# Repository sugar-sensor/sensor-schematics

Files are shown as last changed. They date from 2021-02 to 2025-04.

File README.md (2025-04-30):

# Description
Electrical and mechanical schematics for sugar sensor. 
Includes PCB design and BOM + Gerber files for sensor production
Repository has 2 branches: v1 and v2. Both are based on MAX86141 AFE to work with LEDs. The difference between v1 and v2 are the following:
- v1 uses 3 LEDS (RED, GREEN, BLUE) as light source (non-coherent) while v2 uses 7mW 650nm RED laser (coherent)
- v1 uses AD5933 BioZ controller while v2 uses MAX30002 BioZ controller
- in v2 the main board dependency is removed. Main board replaced with external [TinyPICO](https://www.tinypico.com/) board and add-ons. Sensor board is stackable

## Project notes
1. The main reason to move from v1 to v2 of the sensor board is failed tests on non-coherent light sources. "Failed" means prediction based on these measurements didn't work.
2. Version 2 deprecates "main" folder with all the schematics for main board (controller). Sensor board is stacked with TiniPICO development board and it is stacked with RGB IPS Display shield from add-ons menu.
3. Sensor board programming, testing and obtaining the results is done using [MAX32630FHTR](https://www.analog.com/en/resources/evaluation-hardware-and-software/evaluation-boards-kits/max32630fthr.html) application platform. Development was done in [Mbed Studio](https://os.mbed.com/studio/)

## Structure
- **hull** for the wearable device
- **lib** is custom libraries for KiCad
- **main** is a mainboad schematics. Valid only for v1. Not tested and not produced. 
- **mech** is 3D models for the KiCad component representation on PCB
- **sensor** is sensor schematic, board, BOM, gerbers for production. Both versions were tested and produced

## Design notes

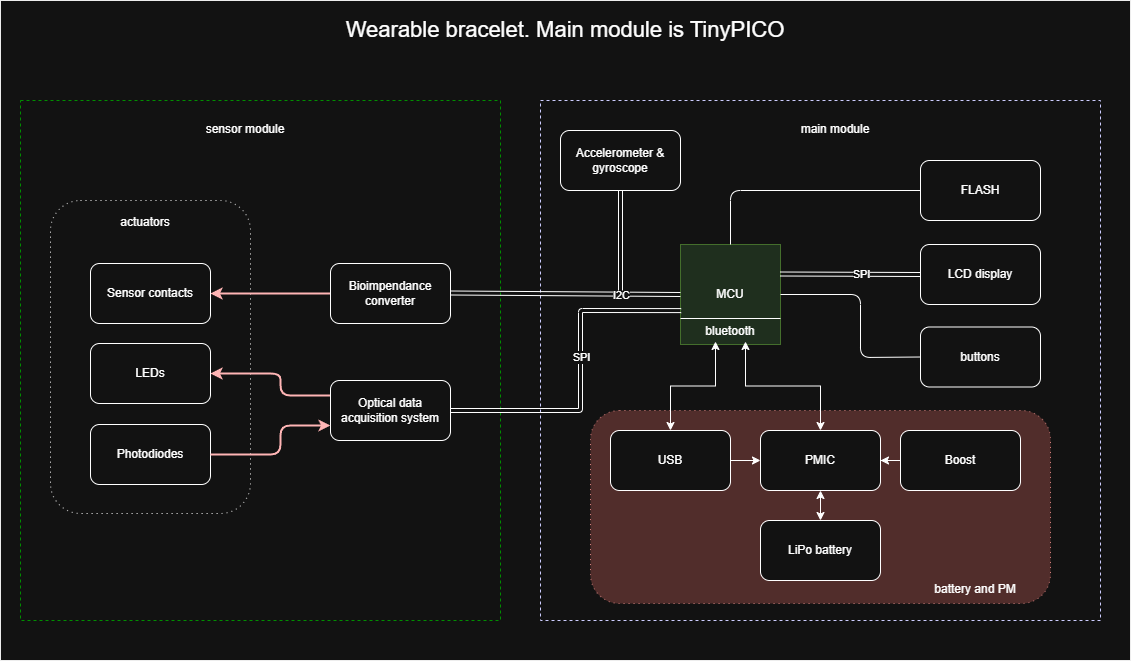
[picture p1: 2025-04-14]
block_diagram.png

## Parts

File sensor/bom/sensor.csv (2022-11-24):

Source: | C:\Users\Vadim\Projects\Horace\sensor\sensor.kicad_sch
Date: | 24.11.2022 15:50:27
Tool: | Eeschema (6.0.8)
Generator: | C:\Program Files\KiCad\6.0\bin\scripting\plugins/bom_csv_grouped_by_value.py
Component Count: | 44
Individual Components:
Item | Qty | Reference(s) | Value | LibPart | Footprint | Datasheet | Arrow Part Number | Arrow Price/Stock | Description | Digikey Part Number | Height | Manufacturer | Manufacturer Part Number | Manufacturer_Name | Manufacturer_Part_Number | Mouser Part Number | Mouser Price/Stock | Mouser part number | Mouser parts/stock | Price
 |  | C1 | 10pF | Device:C_Small | Capacitor_SMD:C_0402_1005Metric | https://www.mouser.ee/datasheet/2/447/UPY-GPHC_X5R_4V-to-50V_25-1131599.pdf |  |  |  | 311-3777-2-ND |  | Yageo | CC0402KRNPO7BN100 |  |  |  | https://www.mouser.ee/ProductDetail/Yageo/CC0402MRX5R5BB106/?qs=zEY9bCHj09eCmUJdZuS5Lg%3D%3D |  |  | 0.1
 |  | C2 | 10pF | Device:C_Small | Capacitor_SMD:C_0402_1005Metric | https://www.mouser.ee/datasheet/2/447/UPY-GPHC_X5R_4V-to-50V_25-1131599.pdf |  |  |  | 311-3777-2-ND |  | Yageo | CC0402KRNPO7BN100 |  |  |  | https://www.mouser.ee/ProductDetail/Yageo/CC0402MRX5R5BB106/?qs=zEY9bCHj09eCmUJdZuS5Lg%3D%3D |  |  | 0.1
 |  | C3 | 47pF | Device:C_Small | Capacitor_SMD:C_0402_1005Metric | https://www.mouser.ee/datasheet/2/447/UPY-GPHC_X5R_4V-to-50V_25-1131599.pdf |  |  |  | 311-3751-2-ND |  | Yageo | CC0402JRNPO8BN470 |  |  |  | https://www.mouser.ee/ProductDetail/Yageo/CC0402MRX5R5BB106/?qs=zEY9bCHj09eCmUJdZuS5Lg%3D%3D |  |  | 0.22
 |  | C4 | 1uF | Device:C_Small | Capacitor_SMD:C_0402_1005Metric | http://www.easyflip.co.uk/Farnell_element14_2013_UK/book.html?page=1145 |  |  |  | 311-1438-2-ND |  | Yageo | CC0402KRX5R5BB105 |  |  |  | https://www.mouser.ee/ProductDetail/Yageo/CC0402KRX5R5BB105/?qs=AgBp2OyFlx8OsRLdvCJiRw%3D%3D |  |  | 0.09
 |  | C5 | 10uF | Device:C_Small | Capacitor_SMD:C_0402_1005Metric | https://www.mouser.ee/datasheet/2/447/UPY-GPHC_X5R_4V-to-50V_25-1131599.pdf |  |  |  | 311-1729-2-ND |  | Yageo | CC0402MRX5R5BB106 |  |  |  | https://www.mouser.ee/ProductDetail/Yageo/CC0402MRX5R5BB106/?qs=zEY9bCHj09eCmUJdZuS5Lg%3D%3D |  |  | 0.22
 |  | C6 | 47nF | Device:C_Small | Capacitor_SMD:C_0402_1005Metric | https://www.mouser.ee/datasheet/2/447/UPY-GPHC_X5R_4V-to-50V_25-1131599.pdf |  |  |  | 311-1688-2-ND |  | Yageo | CC0402KRX5R6BB473 |  |  |  | https://www.mouser.ee/ProductDetail/Yageo/CC0402MRX5R5BB106/?qs=zEY9bCHj09eCmUJdZuS5Lg%3D%3D |  |  | 0.22
 |  | C7 | 47nF | Device:C_Small | Capacitor_SMD:C_0402_1005Metric | https://www.mouser.ee/datasheet/2/447/UPY-GPHC_X5R_4V-to-50V_25-1131599.pdf |  |  |  | 311-1688-2-ND |  | Yageo | CC0402KRX5R6BB473 |  |  |  | https://www.mouser.ee/ProductDetail/Yageo/CC0402MRX5R5BB106/?qs=zEY9bCHj09eCmUJdZuS5Lg%3D%3D |  |  | 0.22
 |  | C8 | 10uF | Device:C_Small | Capacitor_SMD:C_0402_1005Metric | https://www.mouser.ee/datasheet/2/447/UPY-GPHC_X5R_4V-to-50V_25-1131599.pdf |  |  |  | 311-1729-2-ND |  | Yageo | CC0402MRX5R5BB106 |  |  |  | https://www.mouser.ee/ProductDetail/Yageo/CC0402MRX5R5BB106/?qs=zEY9bCHj09eCmUJdZuS5Lg%3D%3D |  |  | 0.22
 |  | C9 | 0.1uF | Device:C_Small | Capacitor_SMD:C_0402_1005Metric | https://www.mouser.ee/datasheet/2/447/UPY-GPHC_X5R_4V-to-50V_25-1131599.pdf |  |  |  | 311-3340-2-ND |  | Yageo | CC0402KRX5R5BB104 |  |  |  | https://www.mouser.ee/ProductDetail/Yageo/CC0402KRX5R5BB104/?qs=T%2F3nPWKqOSbG4z8ii3LyCg%3D%3D |  |  | 0.09
 |  | C10 | 0.1uF | Device:C_Small | Capacitor_SMD:C_0402_1005Metric | https://www.mouser.ee/datasheet/2/447/UPY-GPHC_X5R_4V-to-50V_25-1131599.pdf |  |  |  | 311-3340-2-ND |  | Yageo | CC0402KRX5R5BB104 |  |  |  | https://www.mouser.ee/ProductDetail/Yageo/CC0402KRX5R5BB104/?qs=T%2F3nPWKqOSbG4z8ii3LyCg%3D%3D |  |  | 0.09
 |  | C11 | 1nF | Device:C_Small | Capacitor_SMD:C_0402_1005Metric | https://www.mouser.ee/datasheet/2/447/UPY-GPHC_X5R_4V-to-50V_25-1131599.pdf |  |  |  | 13-CC0402JRNPO7BN102TR-ND |  | Yageo | CC0402JRNPO7BN102 |  |  |  | https://www.mouser.ee/ProductDetail/Yageo/CC0402MRX5R5BB106/?qs=zEY9bCHj09eCmUJdZuS5Lg%3D%3D |  |  | 0.22
 |  | C12 | 10uF | Device:C_Small | Capacitor_SMD:C_0402_1005Metric | https://www.mouser.ee/datasheet/2/447/UPY-GPHC_X5R_4V-to-50V_25-1131599.pdf |  |  |  | 311-1729-2-ND |  | Yageo | CC0402MRX5R5BB106 |  |  |  | https://www.mouser.ee/ProductDetail/Yageo/CC0402MRX5R5BB106/?qs=zEY9bCHj09eCmUJdZuS5Lg%3D%3D |  |  | 0.22
 |  | C13 | 10uF | Device:C_Small | Capacitor_SMD:C_0402_1005Metric | https://www.mouser.ee/datasheet/2/447/UPY-GPHC_X5R_4V-to-50V_25-1131599.pdf |  |  |  | 311-1729-2-ND |  | Yageo | CC0402MRX5R5BB106 |  |  |  | https://www.mouser.ee/ProductDetail/Yageo/CC0402MRX5R5BB106/?qs=zEY9bCHj09eCmUJdZuS5Lg%3D%3D |  |  | 0.22
 |  | C14 | 1uF | Device:C_Small | Capacitor_SMD:C_0402_1005Metric | http://www.easyflip.co.uk/Farnell_element14_2013_UK/book.html?page=1145 |  |  |  | 311-1438-2-ND |  | Yageo | CC0402KRX5R5BB105 |  |  |  | https://www.mouser.ee/ProductDetail/Yageo/CC0402KRX5R5BB105/?qs=AgBp2OyFlx8OsRLdvCJiRw%3D%3D |  |  | 0.09
 |  | C15 | 1uF | Device:C_Small | Capacitor_SMD:C_0402_1005Metric | http://www.easyflip.co.uk/Farnell_element14_2013_UK/book.html?page=1145 |  |  |  | 311-1438-2-ND |  | Yageo | CC0402KRX5R5BB105 |  |  |  | https://www.mouser.ee/ProductDetail/Yageo/CC0402KRX5R5BB105/?qs=AgBp2OyFlx8OsRLdvCJiRw%3D%3D |  |  | 0.09
 |  | C16 | 10uF | Device:C_Small | Capacitor_SMD:C_0402_1005Metric | https://www.mouser.ee/datasheet/2/447/UPY-GPHC_X5R_4V-to-50V_25-1131599.pdf |  |  |  | 311-1729-2-ND |  | Yageo | CC0402MRX5R5BB106 |  |  |  | https://www.mouser.ee/ProductDetail/Yageo/CC0402MRX5R5BB106/?qs=zEY9bCHj09eCmUJdZuS5Lg%3D%3D |  |  | 0.22
 |  | C17 | 1uF | Device:C_Small | Capacitor_SMD:C_0402_1005Metric | http://www.easyflip.co.uk/Farnell_element14_2013_UK/book.html?page=1145 |  |  |  | 311-1438-2-ND |  | Yageo | CC0402KRX5R5BB105 |  |  |  | https://www.mouser.ee/ProductDetail/Yageo/CC0402KRX5R5BB105/?qs=AgBp2OyFlx8OsRLdvCJiRw%3D%3D |  |  | 0.09
 |  | C18 | 1uF | Device:C_Small | Capacitor_SMD:C_0402_1005Metric | http://www.easyflip.co.uk/Farnell_element14_2013_UK/book.html?page=1145 |  |  |  | 311-1438-2-ND |  | Yageo | CC0402KRX5R5BB105 |  |  |  | https://www.mouser.ee/ProductDetail/Yageo/CC0402KRX5R5BB105/?qs=AgBp2OyFlx8OsRLdvCJiRw%3D%3D |  |  | 0.09
 |  | C19 | 0.1uF | Device:C_Small | Capacitor_SMD:C_0402_1005Metric | https://www.mouser.ee/datasheet/2/447/UPY-GPHC_X5R_4V-to-50V_25-1131599.pdf |  |  |  | 311-3340-2-ND |  | Yageo | CC0402KRX5R5BB104 |  |  |  | https://www.mouser.ee/ProductDetail/Yageo/CC0402KRX5R5BB104/?qs=T%2F3nPWKqOSbG4z8ii3LyCg%3D%3D |  |  | 0.09
 |  | C20 | 10uF | Device:C_Small | Capacitor_SMD:C_0402_1005Metric | https://www.mouser.ee/datasheet/2/447/UPY-GPHC_X5R_4V-to-50V_25-1131599.pdf |  |  |  | 311-1729-2-ND |  | Yageo | CC0402MRX5R5BB106 |  |  |  | https://www.mouser.ee/ProductDetail/Yageo/CC0402MRX5R5BB106/?qs=zEY9bCHj09eCmUJdZuS5Lg%3D%3D |  |  | 0.22
 |  | C21 | 1uF | Device:C_Small | Capacitor_SMD:C_0402_1005Metric | http://www.easyflip.co.uk/Farnell_element14_2013_UK/book.html?page=1145 |  |  |  | 311-1438-2-ND |  | Yageo | CC0402KRX5R5BB105 |  |  |  | https://www.mouser.ee/ProductDetail/Yageo/CC0402KRX5R5BB105/?qs=AgBp2OyFlx8OsRLdvCJiRw%3D%3D |  |  | 0.09
 |  | D1 | RLD65NZX1-00A | Horace:RLD65NZX1-00A | Horace:RLD85PZJ400A | https://fscdn.rohm.com/en/products/databook/datasheet/opto/laser_diode/red/rld65pzx300a012-e.pdf |  |  | 635nm Red Single Mode Laser Diode |  | 4.6 |  |  | ROHM Semiconductor | RLD65NZX1-00A | 755-RLD65NZX1-00A | https://www.mouser.co.uk/ProductDetail/ROHM-Semiconductor/RLD65NZX1-00A?qs=vmHwEFxEFR8OdK%252BWr0L3QQ%3D%3D
 |  | D2 | VEMD8081 | Horace:VEMD8081 | Horace:VEMD8081 | https://www.vishay.com/docs/80218/vemd8081.pdf |  |  | High speed and high sensitive PIN photodiode with enhanced sensitivity for visible light, 4.8 x 2.5 x 0.48 package, Radiant sensitive area (in mm2): 5.4 |  | 0.53 |  |  | Vishay | VEMD8081 | 78-VEMD8081 | https://www.mouser.co.uk/ProductDetail/Vishay-Semiconductors/VEMD8081?qs=hd1VzrDQEGhZjg8mME3%2FzQ%3D%3D
 |  | D3 | VEMD8081 | Horace:VEMD8081 | Horace:VEMD8081 | https://www.vishay.com/docs/80218/vemd8081.pdf |  |  | High speed and high sensitive PIN photodiode with enhanced sensitivity for visible light, 4.8 x 2.5 x 0.48 package, Radiant sensitive area (in mm2): 5.4 |  | 0.53 |  |  | Vishay | VEMD8081 | 78-VEMD8081 | https://www.mouser.co.uk/ProductDetail/Vishay-Semiconductors/VEMD8081?qs=hd1VzrDQEGhZjg8mME3%2FzQ%3D%3D
 |  | IC1 | MAX30002CWV+ | Horace:MAX30002CWV+ | Horace:MAX30002CWV | https://componentsearchengine.com/Datasheets/1/MAX30002CWV+.pdf |  |  | Analog Front End - AFE Bio Potential AFE | MAX30002CWV+-ND | 0.69 |  |  | Maxim Integrated | MAX30002CWV+ | 700-MAX30002CWV+ | https://www.mouser.co.uk/ProductDetail/Maxim-Integrated/MAX30002CWV%2b?qs=gTYE2QTfZfRSACHOszRGvQ%3D%3D
 |  | IC2 | LP5900TLX-2.7_NOPB | Horace:LP5900TLX-2.7_NOPB | Horace:BGA4C50P2X2_105X108X68 | http://www.ti.com/lit/gpn/LP5900 |  |  | 150mA Ultralow-Noise LDO for RF and Analog Circuits Requires No Bypass Capacitor |  | 0.675 |  |  | Texas Instruments | LP5900TLX-2.7/NOPB | 926-LP5900TLX27NOPB | https://www.mouser.co.uk/ProductDetail/Texas-Instruments/LP5900TLX-27-NOPB?qs=8uBHJDVwVqwI%252Br0sr7pGhg%3D%3D
 |  | IC3 | MAX86141ENP+T | sensor-rescue:MAX86141ENP+-Horace | Horace:BGA20C40P5X4_205X185X50 | https://www.mouser.ee/datasheet/2/256/MAX86140-1139682.pdf |  |  | MAXIM INTEGRATED PRODUCTS - MAX86141ENP+ - PULSE OXIMETER/HEART RATE SENSOR, WLP-20 | MAX86141ENP+TCT-ND | 0.5 | Maxim Integrated | MAX86141ENP+T | Maxim Integrated | MAX86141ENP+ | 700-MAX86141ENP+T | https://www.mouser.ee/ProductDetail/Maxim-Integrated/MAX86141ENP%2bT?qs=1mbolxNpo8eXAkUx4%252BsdhQ%3D%3D |  |  | 6.25
 |  | IC4 | SIT1532AC | Horace:SIT1532AC-J5-DCC-32.768D | Horace:SIT1532ACJ5DCC32768D | https://www.sitime.com/datasheet/SiT1532 | SIT1532AC-J5-DCC-32.768D | https://www.arrow.com/en/products/sit1532acj5dcc32.768d/sitime?region=nac | Oscillator MEMS 0.032768MHz +/-75ppm (Stability) LVCMOS 52% 1.8V/2.5V/3.3V 4-Pin CSP SMD T/R |  | 0.6 |  |  | SiTime | SIT1532AC-J5-DCC-32.768D | 788-1532ACJ5DCC32.7D | https://www.mouser.co.uk/ProductDetail/SiTime/SIT1532AC-J5-DCC-32768D?qs=dMZC7um9hO%2FgFQ4wFMXsCg%3D%3D
 |  | IC5 | LP5900TLX-1.8_NOPB | Horace:LP5900TLX-2.7_NOPB | Horace:BGA4C50P2X2_105X108X68 | http://www.ti.com/lit/gpn/LP5900 |  |  | 150mA Ultralow-Noise LDO for RF and Analog Circuits Requires No Bypass Capacitor |  | 0.675 |  |  | Texas Instruments | LP5900TLX-2.7/NOPB | 926-LP5900TLX27NOPB | https://www.mouser.co.uk/ProductDetail/Texas-Instruments/LP5900TLX-27-NOPB?qs=8uBHJDVwVqwI%252Br0sr7pGhg%3D%3D
 |  | J1 | Conn_01x10_Female | Connector:Conn_01x10_Female | Connector_PinSocket_2.54mm:PinSocket_1x10_P2.54mm_Vertical | https://www.mouser.ee/datasheet/2/276/3/0901471110_PCB_RECEPTACLES-2871466.pdf |  |  |  |  |  | Molex | 90147-1110 |  |  |  |  | 538-90147-1110 | https://www.mouser.ee/ProductDetail/Molex/90147-1110
 |  | J2 | Conn_01x10_Female | Connector:Conn_01x10_Female | Connector_PinSocket_2.54mm:PinSocket_1x10_P2.54mm_Vertical | https://www.mouser.ee/datasheet/2/276/3/0901471110_PCB_RECEPTACLES-2871466.pdf |  |  |  |  |  | Molex | 90147-1110 |  |  |  |  | 538-90147-1110 | https://www.mouser.ee/ProductDetail/Molex/90147-1110
 |  | J3 | Probe_01_male | sensor-rescue:Probe_01_male-Horace | Horace:Probe_01_male | https://www.mouser.ee/datasheet/2/273/223.7-1519985.pdf |  |  |  | ED10387-ND |  |  | 3977-1-00-15-00-00-03-0 |  |  |  | https://www.digikey.ee/products/en?keywords=3975-0-00-15-00-00-03-0 |  |  | 0.3
 |  | J4 | Probe_01_male | sensor-rescue:Probe_01_male-Horace | Horace:Probe_01_male | https://www.mouser.ee/datasheet/2/273/223.7-1519985.pdf |  |  |  | ED10387-ND |  |  | 3977-1-00-15-00-00-03-0 |  |  |  | https://www.digikey.ee/products/en?keywords=3975-0-00-15-00-00-03-0 |  |  | 0.3
 |  | J5 | Probe_01_male | sensor-rescue:Probe_01_male-Horace | Horace:Probe_01_male | https://www.mouser.ee/datasheet/2/273/223.7-1519985.pdf |  |  |  | ED10387-ND |  |  | 3977-1-00-15-00-00-03-0 |  |  |  | https://www.digikey.ee/products/en?keywords=3975-0-00-15-00-00-03-0 |  |  | 0.3
 |  | J6 | Probe_01_male | sensor-rescue:Probe_01_male-Horace | Horace:Probe_01_male | https://www.mouser.ee/datasheet/2/273/223.7-1519985.pdf |  |  |  | ED10387-ND |  |  | 3977-1-00-15-00-00-03-0 |  |  |  | https://www.digikey.ee/products/en?keywords=3975-0-00-15-00-00-03-0 |  |  | 0.3
 |  | R1 | 200 | Device:R_Small | Resistor_SMD:R_0402_1005Metric | https://www.mouser.ee/datasheet/2/427/crcwce3-1762584.pdf |  |  |  | 541-3995-2-ND |  | Vishay / Dale | CRCW0402200RFKEDC |  |  |  | https://www.mouser.ee/ProductDetail/Vishay-Dale/CRCW0402200RFKEDC?qs=E3Y5ESvWgWP6CT2hjJxX9A%3D%3D |  |  | 0.09
 |  | R2 | 200 | Device:R_Small | Resistor_SMD:R_0402_1005Metric | https://www.mouser.ee/datasheet/2/427/crcwce3-1762584.pdf |  |  |  | 541-3995-2-ND |  | Vishay / Dale | CRCW0402200RFKEDC |  |  |  | https://www.mouser.ee/ProductDetail/Vishay-Dale/CRCW0402200RFKEDC?qs=E3Y5ESvWgWP6CT2hjJxX9A%3D%3D |  |  | 0.09
 |  | R3 | 324k | Device:R_Small | Resistor_SMD:R_0402_1005Metric | https://www.mouser.ee/datasheet/2/427/crcwce3-1762584.pdf |  |  |  | 541-4894-2-ND |  | Vishay / Dale | CRCW0402324KFKEDC |  |  |  | https://www.mouser.ee/ProductDetail/Vishay-Dale/CRCW0402324KFKEDC?qs=E3Y5ESvWgWPWxHcYNHkI3g%3D%3D |  |  | 0.2
 |  | R4 | 0 | Device:R_Small | Resistor_SMD:R_0402_1005Metric | https://www.mouser.ee/datasheet/2/427/crcwce3-1762584.pdf |  |  |  | 541-4062-2-ND |  | Vishay / Dale | CRCW04020000Z0EDC |  |  |  | https://www.mouser.ee/ProductDetail/Vishay-Dale/CRCW04020000Z0EDC/ |  |  | 0.09
 |  | R5 | 1k | Device:R_Small | Resistor_SMD:R_0402_1005Metric | https://www.mouser.ee/datasheet/2/427/crcwce3-1762584.pdf |  |  |  | 541-3961-2-ND |  | Vishay / Dale | CRCW04021K00FKEDC |  |  |  | https://www.mouser.ee/ProductDetail/Vishay-Dale/CRCW04021K00FKEDC |  |  | 0.09
 |  | R6 | 1k | Device:R_Small | Resistor_SMD:R_0402_1005Metric | https://www.mouser.ee/datasheet/2/427/crcwce3-1762584.pdf |  |  |  | 541-3961-2-ND |  | Vishay / Dale | CRCW04021K00FKEDC |  |  |  | https://www.mouser.ee/ProductDetail/Vishay-Dale/CRCW04021K00FKEDC |  |  | 0.09
 |  | R7 | 1k | Device:R_Small | Resistor_SMD:R_0402_1005Metric | https://www.mouser.ee/datasheet/2/427/crcwce3-1762584.pdf |  |  |  | 541-3961-2-ND |  | Vishay / Dale | CRCW04021K00FKEDC |  |  |  | https://www.mouser.ee/ProductDetail/Vishay-Dale/CRCW04021K00FKEDC |  |  | 0.09
 |  | R8 | 0 | Device:R_Small | Resistor_SMD:R_0402_1005Metric | https://www.mouser.ee/datasheet/2/427/crcwce3-1762584.pdf |  |  |  | 541-4062-2-ND |  | Vishay / Dale | CRCW04020000Z0EDC |  |  |  | https://www.mouser.ee/ProductDetail/Vishay-Dale/CRCW04020000Z0EDC/ |  |  | 0.09
 |  | R9 | 0 | Device:R_Small | Resistor_SMD:R_0402_1005Metric | https://www.mouser.ee/datasheet/2/427/crcwce3-1762584.pdf |  |  |  | 541-4062-2-ND |  | Vishay / Dale | CRCW04020000Z0EDC |  |  |  | https://www.mouser.ee/ProductDetail/Vishay-Dale/CRCW04020000Z0EDC/ |  |  | 0.09
Collated Components:
Item | Qty | Reference(s) | Value | LibPart | Footprint | Datasheet | Arrow Part Number | Arrow Price/Stock | Description | Digikey Part Number | Height | Manufacturer | Manufacturer Part Number | Manufacturer_Name | Manufacturer_Part_Number | Mouser Part Number | Mouser Price/Stock | Mouser part number | Mouser parts/stock | Price
1 | 2 | C1, C2 | 10pF | Device:C_Small | Capacitor_SMD:C_0402_1005Metric | https://www.mouser.ee/datasheet/2/447/UPY-GPHC_X5R_4V-to-50V_25-1131599.pdf |  |  |  | 311-3777-2-ND |  | Yageo | CC0402KRNPO7BN100 |  |  |  | https://www.mouser.ee/ProductDetail/Yageo/CC0402MRX5R5BB106/?qs=zEY9bCHj09eCmUJdZuS5Lg%3D%3D |  |  | 0.1
2 | 1 | C3 | 47pF | Device:C_Small | Capacitor_SMD:C_0402_1005Metric | https://www.mouser.ee/datasheet/2/447/UPY-GPHC_X5R_4V-to-50V_25-1131599.pdf |  |  |  | 311-3751-2-ND |  | Yageo | CC0402JRNPO8BN470 |  |  |  | https://www.mouser.ee/ProductDetail/Yageo/CC0402MRX5R5BB106/?qs=zEY9bCHj09eCmUJdZuS5Lg%3D%3D |  |  | 0.22
3 | 6 | C4, C14, C15, C17, C18, C21 | 1uF | Device:C_Small | Capacitor_SMD:C_0402_1005Metric | http://www.easyflip.co.uk/Farnell_element14_2013_UK/book.html?page=1145 |  |  |  | 311-1438-2-ND |  | Yageo | CC0402KRX5R5BB105 |  |  |  | https://www.mouser.ee/ProductDetail/Yageo/CC0402KRX5R5BB105/?qs=AgBp2OyFlx8OsRLdvCJiRw%3D%3D |  |  | 0.09
4 | 6 | C5, C8, C12, C13, C16, C20 | 10uF | Device:C_Small | Capacitor_SMD:C_0402_1005Metric | https://www.mouser.ee/datasheet/2/447/UPY-GPHC_X5R_4V-to-50V_25-1131599.pdf |  |  |  | 311-1729-2-ND |  | Yageo | CC0402MRX5R5BB106 |  |  |  | https://www.mouser.ee/ProductDetail/Yageo/CC0402MRX5R5BB106/?qs=zEY9bCHj09eCmUJdZuS5Lg%3D%3D |  |  | 0.22
5 | 2 | C6, C7 | 47nF | Device:C_Small | Capacitor_SMD:C_0402_1005Metric | https://www.mouser.ee/datasheet/2/447/UPY-GPHC_X5R_4V-to-50V_25-1131599.pdf |  |  |  | 311-1688-2-ND |  | Yageo | CC0402KRX5R6BB473 |  |  |  | https://www.mouser.ee/ProductDetail/Yageo/CC0402MRX5R5BB106/?qs=zEY9bCHj09eCmUJdZuS5Lg%3D%3D |  |  | 0.22
6 | 3 | C9, C10, C19 | 0.1uF | Device:C_Small | Capacitor_SMD:C_0402_1005Metric | https://www.mouser.ee/datasheet/2/447/UPY-GPHC_X5R_4V-to-50V_25-1131599.pdf |  |  |  | 311-3340-2-ND |  | Yageo | CC0402KRX5R5BB104 |  |  |  | https://www.mouser.ee/ProductDetail/Yageo/CC0402KRX5R5BB104/?qs=T%2F3nPWKqOSbG4z8ii3LyCg%3D%3D |  |  | 0.09
7 | 1 | C11 | 1nF | Device:C_Small | Capacitor_SMD:C_0402_1005Metric | https://www.mouser.ee/datasheet/2/447/UPY-GPHC_X5R_4V-to-50V_25-1131599.pdf |  |  |  | 13-CC0402JRNPO7BN102TR-ND |  | Yageo | CC0402JRNPO7BN102 |  |  |  | https://www.mouser.ee/ProductDetail/Yageo/CC0402MRX5R5BB106/?qs=zEY9bCHj09eCmUJdZuS5Lg%3D%3D |  |  | 0.22
8 | 1 | D1 | RLD65NZX1-00A | Horace:RLD65NZX1-00A | Horace:RLD85PZJ400A | https://fscdn.rohm.com/en/products/databook/datasheet/opto/laser_diode/red/rld65pzx300a012-e.pdf |  |  | 635nm Red Single Mode Laser Diode |  | 4.6 |  |  | ROHM Semiconductor | RLD65NZX1-00A | 755-RLD65NZX1-00A | https://www.mouser.co.uk/ProductDetail/ROHM-Semiconductor/RLD65NZX1-00A?qs=vmHwEFxEFR8OdK%252BWr0L3QQ%3D%3D
9 | 2 | D2, D3 | VEMD8081 | Horace:VEMD8081 | Horace:VEMD8081 | https://www.vishay.com/docs/80218/vemd8081.pdf |  |  | High speed and high sensitive PIN photodiode with enhanced sensitivity for visible light, 4.8 x 2.5 x 0.48 package, Radiant sensitive area (in mm2): 5.4 |  | 0.53 |  |  | Vishay | VEMD8081 | 78-VEMD8081 | https://www.mouser.co.uk/ProductDetail/Vishay-Semiconductors/VEMD8081?qs=hd1VzrDQEGhZjg8mME3%2FzQ%3D%3D
10 | 1 | IC1 | MAX30002CWV+ | Horace:MAX30002CWV+ | Horace:MAX30002CWV | https://componentsearchengine.com/Datasheets/1/MAX30002CWV+.pdf |  |  | Analog Front End - AFE Bio Potential AFE | MAX30002CWV+-ND | 0.69 |  |  | Maxim Integrated | MAX30002CWV+ | 700-MAX30002CWV+ | https://www.mouser.co.uk/ProductDetail/Maxim-Integrated/MAX30002CWV%2b?qs=gTYE2QTfZfRSACHOszRGvQ%3D%3D
11 | 1 | IC2 | LP5900TLX-2.7_NOPB | Horace:LP5900TLX-2.7_NOPB | Horace:BGA4C50P2X2_105X108X68 | http://www.ti.com/lit/gpn/LP5900 |  |  | 150mA Ultralow-Noise LDO for RF and Analog Circuits Requires No Bypass Capacitor |  | 0.675 |  |  | Texas Instruments | LP5900TLX-2.7/NOPB | 926-LP5900TLX27NOPB | https://www.mouser.co.uk/ProductDetail/Texas-Instruments/LP5900TLX-27-NOPB?qs=8uBHJDVwVqwI%252Br0sr7pGhg%3D%3D
12 | 1 | IC3 | MAX86141ENP+T | sensor-rescue:MAX86141ENP+-Horace | Horace:BGA20C40P5X4_205X185X50 | https://www.mouser.ee/datasheet/2/256/MAX86140-1139682.pdf |  |  | MAXIM INTEGRATED PRODUCTS - MAX86141ENP+ - PULSE OXIMETER/HEART RATE SENSOR, WLP-20 | MAX86141ENP+TCT-ND | 0.5 | Maxim Integrated | MAX86141ENP+T | Maxim Integrated | MAX86141ENP+ | 700-MAX86141ENP+T | https://www.mouser.ee/ProductDetail/Maxim-Integrated/MAX86141ENP%2bT?qs=1mbolxNpo8eXAkUx4%252BsdhQ%3D%3D |  |  | 6.25
13 | 1 | IC4 | SIT1532AC | Horace:SIT1532AC-J5-DCC-32.768D | Horace:SIT1532ACJ5DCC32768D | https://www.sitime.com/datasheet/SiT1532 | SIT1532AC-J5-DCC-32.768D | https://www.arrow.com/en/products/sit1532acj5dcc32.768d/sitime?region=nac | Oscillator MEMS 0.032768MHz +/-75ppm (Stability) LVCMOS 52% 1.8V/2.5V/3.3V 4-Pin CSP SMD T/R |  | 0.6 |  |  | SiTime | SIT1532AC-J5-DCC-32.768D | 788-1532ACJ5DCC32.7D | https://www.mouser.co.uk/ProductDetail/SiTime/SIT1532AC-J5-DCC-32768D?qs=dMZC7um9hO%2FgFQ4wFMXsCg%3D%3D
14 | 1 | IC5 | LP5900TLX-1.8_NOPB | Horace:LP5900TLX-2.7_NOPB | Horace:BGA4C50P2X2_105X108X68 | http://www.ti.com/lit/gpn/LP5900 |  |  | 150mA Ultralow-Noise LDO for RF and Analog Circuits Requires No Bypass Capacitor |  | 0.675 |  |  | Texas Instruments | LP5900TLX-2.7/NOPB | 926-LP5900TLX27NOPB | https://www.mouser.co.uk/ProductDetail/Texas-Instruments/LP5900TLX-27-NOPB?qs=8uBHJDVwVqwI%252Br0sr7pGhg%3D%3D
15 | 2 | J1, J2 | Conn_01x10_Female | Connector:Conn_01x10_Female | Connector_PinSocket_2.54mm:PinSocket_1x10_P2.54mm_Vertical | https://www.mouser.ee/datasheet/2/276/3/0901471110_PCB_RECEPTACLES-2871466.pdf |  |  |  |  |  | Molex | 90147-1110 |  |  |  |  | 538-90147-1110 | https://www.mouser.ee/ProductDetail/Molex/90147-1110
16 | 4 | J3, J4, J5, J6 | Probe_01_male | sensor-rescue:Probe_01_male-Horace | Horace:Probe_01_male | https://www.mouser.ee/datasheet/2/273/223.7-1519985.pdf |  |  |  | ED10387-ND |  |  | 3977-1-00-15-00-00-03-0 |  |  |  | https://www.digikey.ee/products/en?keywords=3975-0-00-15-00-00-03-0 |  |  | 0.3
17 | 2 | R1, R2 | 200 | Device:R_Small | Resistor_SMD:R_0402_1005Metric | https://www.mouser.ee/datasheet/2/427/crcwce3-1762584.pdf |  |  |  | 541-3995-2-ND |  | Vishay / Dale | CRCW0402200RFKEDC |  |  |  | https://www.mouser.ee/ProductDetail/Vishay-Dale/CRCW0402200RFKEDC?qs=E3Y5ESvWgWP6CT2hjJxX9A%3D%3D |  |  | 0.09
18 | 1 | R3 | 324k | Device:R_Small | Resistor_SMD:R_0402_1005Metric | https://www.mouser.ee/datasheet/2/427/crcwce3-1762584.pdf |  |  |  | 541-4894-2-ND |  | Vishay / Dale | CRCW0402324KFKEDC |  |  |  | https://www.mouser.ee/ProductDetail/Vishay-Dale/CRCW0402324KFKEDC?qs=E3Y5ESvWgWPWxHcYNHkI3g%3D%3D |  |  | 0.2
19 | 3 | R4, R8, R9 | 0 | Device:R_Small | Resistor_SMD:R_0402_1005Metric | https://www.mouser.ee/datasheet/2/427/crcwce3-1762584.pdf |  |  |  | 541-4062-2-ND |  | Vishay / Dale | CRCW04020000Z0EDC |  |  |  | https://www.mouser.ee/ProductDetail/Vishay-Dale/CRCW04020000Z0EDC/ |  |  | 0.09
20 | 3 | R5, R6, R7 | 1k | Device:R_Small | Resistor_SMD:R_0402_1005Metric | https://www.mouser.ee/datasheet/2/427/crcwce3-1762584.pdf |  |  |  | 541-3961-2-ND |  | Vishay / Dale | CRCW04021K00FKEDC |  |  |  | https://www.mouser.ee/ProductDetail/Vishay-Dale/CRCW04021K00FKEDC |  |  | 0.09

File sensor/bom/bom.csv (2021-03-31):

Reference | Value | Footprint | Datasheet | Digikey Part Number | Manufacturer | Manufacturer Part Number | Mouser Price/Stock | Price | Description | Digikey_ref | Height | Manufacturer Name | Mouser Part Number | Arrow Part Number | Arrow Price/Stock
C4 | 22uF | Capacitor_SMD:C_0402_1005Metric | https://www.mouser.ee/datasheet/2/447/UPY-GPHC_X5R_4V-to-50V_25-1131599.pdf | 311-3479-2-ND | Yageo | CC0402MRX5R5BB226 | https://www.mouser.ee/ProductDetail/Yageo/CC0402MRX5R5BB226/?qs=1mbolxNpo8feUBij0j9URA%3D%3D | 0.38
C3 | 1uF | Capacitor_SMD:C_0402_1005Metric | http://www.easyflip.co.uk/Farnell_element14_2013_UK/book.html?page=1145 | 311-1438-2-ND | Yageo | CC0402KRX5R5BB105 | https://www.mouser.ee/ProductDetail/Yageo/CC0402KRX5R5BB105/?qs=AgBp2OyFlx8OsRLdvCJiRw%3D%3D | 0.09
C6 | 10uF | Capacitor_SMD:C_0402_1005Metric | https://www.mouser.ee/datasheet/2/447/UPY-GPHC_X5R_4V-to-50V_25-1131599.pdf | 311-1729-2-ND | Yageo | CC0402MRX5R5BB106 | https://www.mouser.ee/ProductDetail/Yageo/CC0402MRX5R5BB106/?qs=zEY9bCHj09eCmUJdZuS5Lg%3D%3D | 0.22
C5 | 0.1uF | Capacitor_SMD:C_0402_1005Metric | https://www.mouser.ee/datasheet/2/447/UPY-GPHC_X5R_4V-to-50V_25-1131599.pdf | 311-3340-2-ND | Yageo | CC0402KRX5R5BB104 | https://www.mouser.ee/ProductDetail/Yageo/CC0402KRX5R5BB104/?qs=T%2F3nPWKqOSbG4z8ii3LyCg%3D%3D | 0.09
R8 | 1k | Resistor_SMD:R_0402_1005Metric | https://www.mouser.ee/datasheet/2/427/crcw01005e3-1762154.pdf | 541-4279-2-ND | Vishay / Dale | CRCW01001K00JREL | https://www.mouser.ee/ProductDetail/Vishay-Dale/CRCW01001K00JREL/ | 0.14
R7 | 1k | Resistor_SMD:R_0402_1005Metric | https://www.mouser.ee/datasheet/2/427/crcw01005e3-1762154.pdf | 541-4279-2-ND | Vishay / Dale | CRCW01001K00JREL | https://www.mouser.ee/ProductDetail/Vishay-Dale/CRCW01001K00JREL/?qs=3CaSHoNeR5tPjJyYZZWXXA%3D%3D | 0.14
R9 | 1k | Resistor_SMD:R_0402_1005Metric | https://www.mouser.ee/datasheet/2/427/crcw01005e3-1762154.pdf | 541-4279-2-ND | Vishay / Dale | CRCW01001K00JREL | https://www.mouser.ee/ProductDetail/Vishay-Dale/CRCW01001K00JREL/ | 0.14
R4 | 10k | Resistor_SMD:R_0402_1005Metric | https://www.mouser.ee/datasheet/2/427/crcw01005e3-1762154.pdf | 541-4276-2-ND | Vishay / Dale | CRCW010010K0JREL | https://www.mouser.ee/ProductDetail/Vishay-Dale/CRCW010010K0JREL/ | 0.14
R6 | 1k | Resistor_SMD:R_0402_1005Metric | https://www.mouser.ee/datasheet/2/427/crcw01005e3-1762154.pdf | 541-4279-2-ND | Vishay / Dale | CRCW01001K00JREL | https://www.mouser.ee/ProductDetail/Vishay-Dale/CRCW01001K00JREL/ | 0.14
C2 | 10pF | Capacitor_SMD:C_0402_1005Metric | https://www.mouser.ee/datasheet/2/447/yageo_yago_s_a0009251638_1-1991554.pdf | 311-1640-2-ND | Yageo | CC0402FRNPO9BN100 | https://www.mouser.ee/ProductDetail/Yageo/CC0402FRNPO9BN100 | 0.09
C1 | 10uF | Capacitor_SMD:C_0402_1005Metric | https://www.mouser.ee/datasheet/2/447/UPY-GPHC_X5R_4V-to-50V_25-1131599.pdf | 311-1729-2-ND | Yageo | CC0402MRX5R5BB106 | https://www.mouser.ee/ProductDetail/Yageo/CC0402MRX5R5BB106/?qs=zEY9bCHj09eCmUJdZuS5Lg%3D%3D | 0.22
J1 | 502078-1710 | 5020781710 | https://componentsearchengine.com/Datasheets/2/502078-1710.pdf | WM14446TR-ND |  | 502078-1710 | https://www.mouser.co.uk/ProductDetail/Molex/502078-1710/?qs=qM7ngqbhX5VeJKt0xqlhhA%3D%3D | 1.68 | 250UM FPC E/O Hsg Assy 17Ckt EmbsTpPkg | https://www.digikey.com/en/products/detail/molex/5020781710/2818915?s=N4IgTCBcDaIKwAYwIOwA4C0BGFWEgF0BfIA | 1.15 | Molex | 538-502078-1710
D2 | VEMD8080 | VEMD8080 | https://www.vishay.com/docs/84565/vemd8080.pdf | VEMD8080TR-ND | Vishay | VEMD8080 | https://www.mouser.co.uk/ProductDetail/Vishay-Semiconductors/VEMD8080?qs=F5EMLAvA7IBCchs2bw9l%2Fw%3D%3D | 1.75 | Photodiodes Pin Photodiode 20V 350-1100nm; 28uA |  | 0.53 |  | 78-VEMD8080 | VEMD8080 | https://www.arrow.com/en/products/vemd8080/vishay
IC1 | AD5933YRSZ | SOP65P780X200-16N | http://www.analog.com/static/imported-files/data_sheets/AD5933.pdf | AD5933YRSZ-ND | Analog Devices | AD5933YRSZ | https://www.mouser.co.uk/ProductDetail/Analog-Devices/AD5933YRSZ?qs=NmRFExCfTkHN0vttR%252B%2Fp9A%3D%3D | 30.46 | AD5933YRSZ, Impedance Converter, 16-Pin SSOP |  | 2 |  | 584-AD5933YRSZ | AD5933YRSZ | https://www.arrow.com/en/products/ad5933yrsz/analog-devices
D3 | VEMD8080 | VEMD8080 | https://www.vishay.com/docs/84565/vemd8080.pdf | VEMD8080TR-ND | Vishay | VEMD8080 | https://www.mouser.co.uk/ProductDetail/Vishay-Semiconductors/VEMD8080?qs=F5EMLAvA7IBCchs2bw9l%2Fw%3D%3D | 1.75 | Photodiodes Pin Photodiode 20V 350-1100nm; 28uA |  | 0.53 |  | 78-VEMD8080 | VEMD8080 | https://www.arrow.com/en/products/vemd8080/vishay
IC2 | MAX86141ENP+T | BGA20C40P5X4_205X185X50 | https://www.mouser.ee/datasheet/2/256/MAX86140-1139682.pdf | MAX86141ENP+TCT-ND | Maxim Integrated | MAX86141ENP+T | https://www.mouser.ee/ProductDetail/Maxim-Integrated/MAX86141ENP%2bT?qs=1mbolxNpo8eXAkUx4%252BsdhQ%3D%3D | 6.25 | MAXIM INTEGRATED PRODUCTS - MAX86141ENP+ - PULSE OXIMETER/HEART RATE SENSOR, WLP-20 |  | 0.5 |  | 700-MAX86141ENP+T
L1 | LQW15DN150M00D | Horace:LQW15DN150M00D | https://psearch.en.murata.com/inductor/product/LQW15DN150M00%23.html | 490-18069-2-ND | Murata Electronics | LQW15DN150M00D | https://www.mouser.co.uk/ProductDetail/Murata-Electronics/LQW15DN150M00D?qs=55YtniHzbhAjiaw66ArnFg%3D%3D | 1.9 | LQW15DN_00 Series Inductor 15uH +/-20% 0402 (1005) |  | 0.7 |  | 81-LQW15DN150M00D
R5 | 0 | Resistor_SMD:R_0402_1005Metric | https://www.mouser.ee/datasheet/2/427/crcwce3-1762584.pdf | 541-4062-2-ND | Vishay / Dale | CRCW04020000Z0EDC | https://www.mouser.ee/ProductDetail/Vishay-Dale/CRCW04020000Z0EDC/ | 0.09
R3 | 10k | Resistor_SMD:R_0402_1005Metric | https://www.mouser.ee/datasheet/2/427/crcw01005e3-1762154.pdf | 541-4276-2-ND | Vishay / Dale | CRCW010010K0JREL | https://www.mouser.ee/ProductDetail/Vishay-Dale/CRCW010010K0JREL/ | 0.14
R1 | 0 | Resistor_SMD:R_0402_1005Metric | https://www.mouser.ee/datasheet/2/427/crcwce3-1762584.pdf | 541-4062-2-ND | Vishay / Dale | CRCW04020000Z0EDC | https://www.mouser.ee/ProductDetail/Vishay-Dale/CRCW04020000Z0EDC/ | 0.09
R2 | 0 | Resistor_SMD:R_0402_1005Metric | https://www.mouser.ee/datasheet/2/427/crcwce3-1762584.pdf | 541-4062-2-ND | Vishay / Dale | CRCW04020000Z0EDC | https://www.mouser.ee/ProductDetail/Vishay-Dale/CRCW04020000Z0EDC/ | 0.09
J5 | Probe_01_male | Horace:Probe_01_male | https://www.mouser.ee/datasheet/2/273/223.7-1519985.pdf | ED10387-ND |  |  | https://www.digikey.ee/products/en?keywords=3975-0-00-15-00-00-03-0 | 0.3
J3 | Probe_01_male | Horace:Probe_01_male | https://www.mouser.ee/datasheet/2/273/223.7-1519985.pdf | ED10387-ND |  |  | https://www.digikey.ee/products/en?keywords=3975-0-00-15-00-00-03-0 | 0.3
J4 | Probe_01_male | Horace:Probe_01_male | https://www.mouser.ee/datasheet/2/273/223.7-1519985.pdf | ED10387-ND |  |  | https://www.digikey.ee/products/en?keywords=3975-0-00-15-00-00-03-0 | 0.3
J2 | Probe_01_male | Horace:Probe_01_male | https://www.mouser.ee/datasheet/2/273/223.7-1519985.pdf | ED10387-ND |  |  | https://www.digikey.ee/products/en?keywords=3975-0-00-15-00-00-03-0 | 0.3
LED1 | 150352M173300 | Horace:150352M173300 | https://www.mouser.ee/datasheet/2/445/150352M173300-1714664.pdf | 732-11999-1-ND |  | 150352M173300 | https://www.mouser.ee/ProductDetail/Wurth-Elektronik/150352M173300 | 0.53
R10 | 0 | Resistor_SMD:R_0402_1005Metric | https://www.mouser.ee/datasheet/2/427/crcwce3-1762584.pdf | 541-4062-2-ND | Vishay / Dale | CRCW04020000Z0EDC | https://www.mouser.ee/ProductDetail/Vishay-Dale/CRCW04020000Z0EDC/ | 0.09

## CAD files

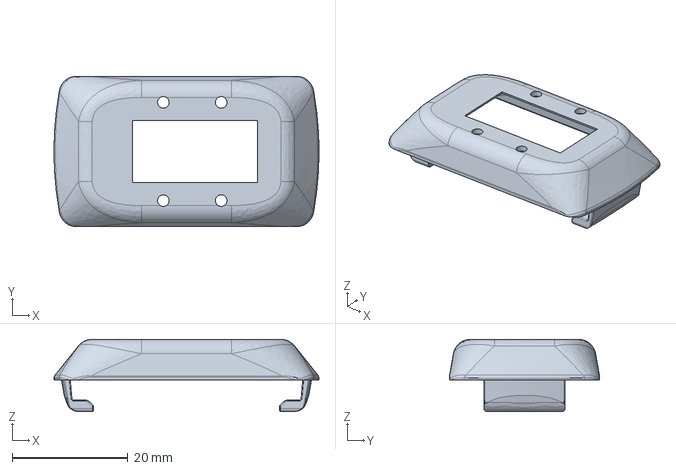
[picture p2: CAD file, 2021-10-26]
hull/top_cover_v2_1.stp
45.9 x 26.0 x 12.5 mm

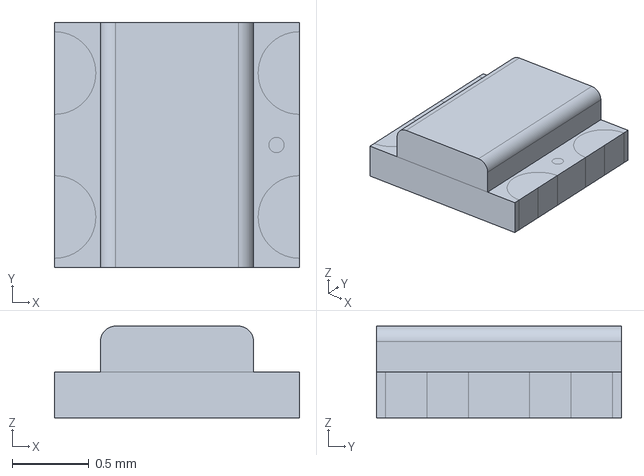
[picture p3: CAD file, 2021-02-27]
mech/KRTB-EILQ51.3A.FCStd
1.60 x 1.60 x 0.6 mm

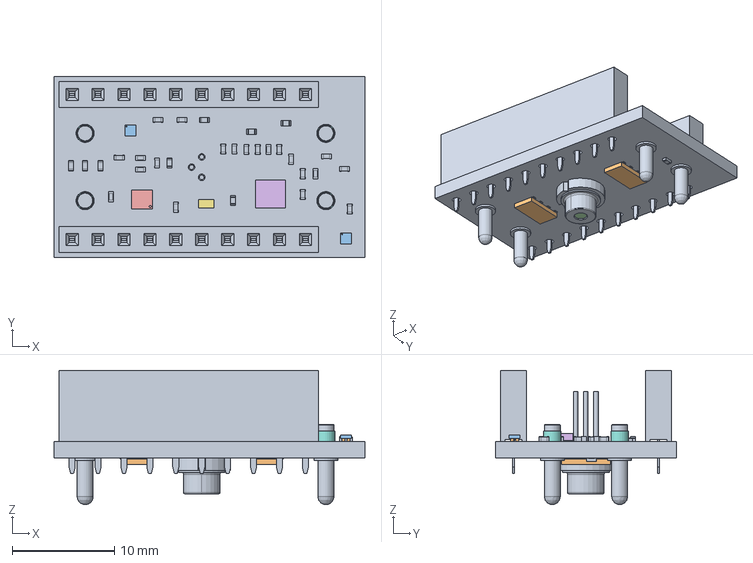
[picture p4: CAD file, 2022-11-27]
sensor/3d/sensor.step
30.5 x 17.8 x 13.2 mm

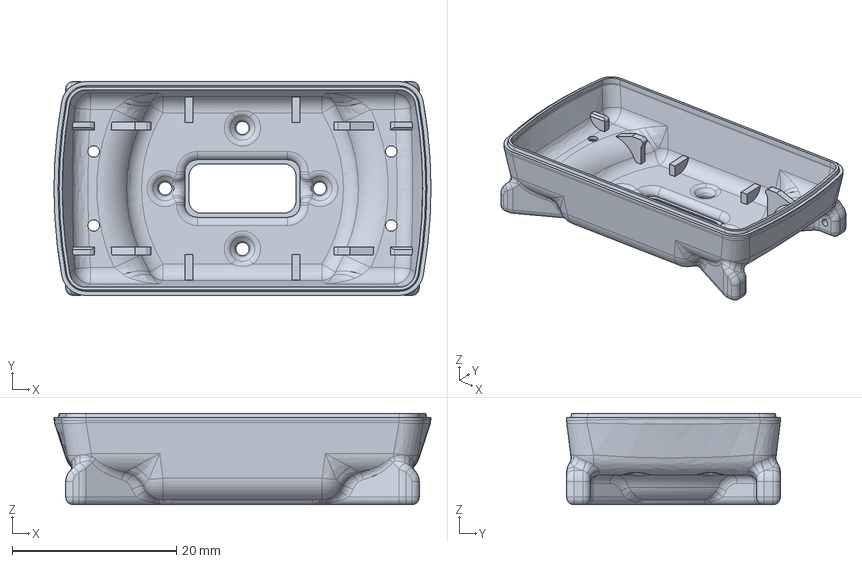
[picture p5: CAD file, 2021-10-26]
hull/back_cover_v2_1.stp
45.9 x 26.0 x 11.1 mm

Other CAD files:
hull/back_cover_v2_1.stl
hull/top_cover_v2_1.stl

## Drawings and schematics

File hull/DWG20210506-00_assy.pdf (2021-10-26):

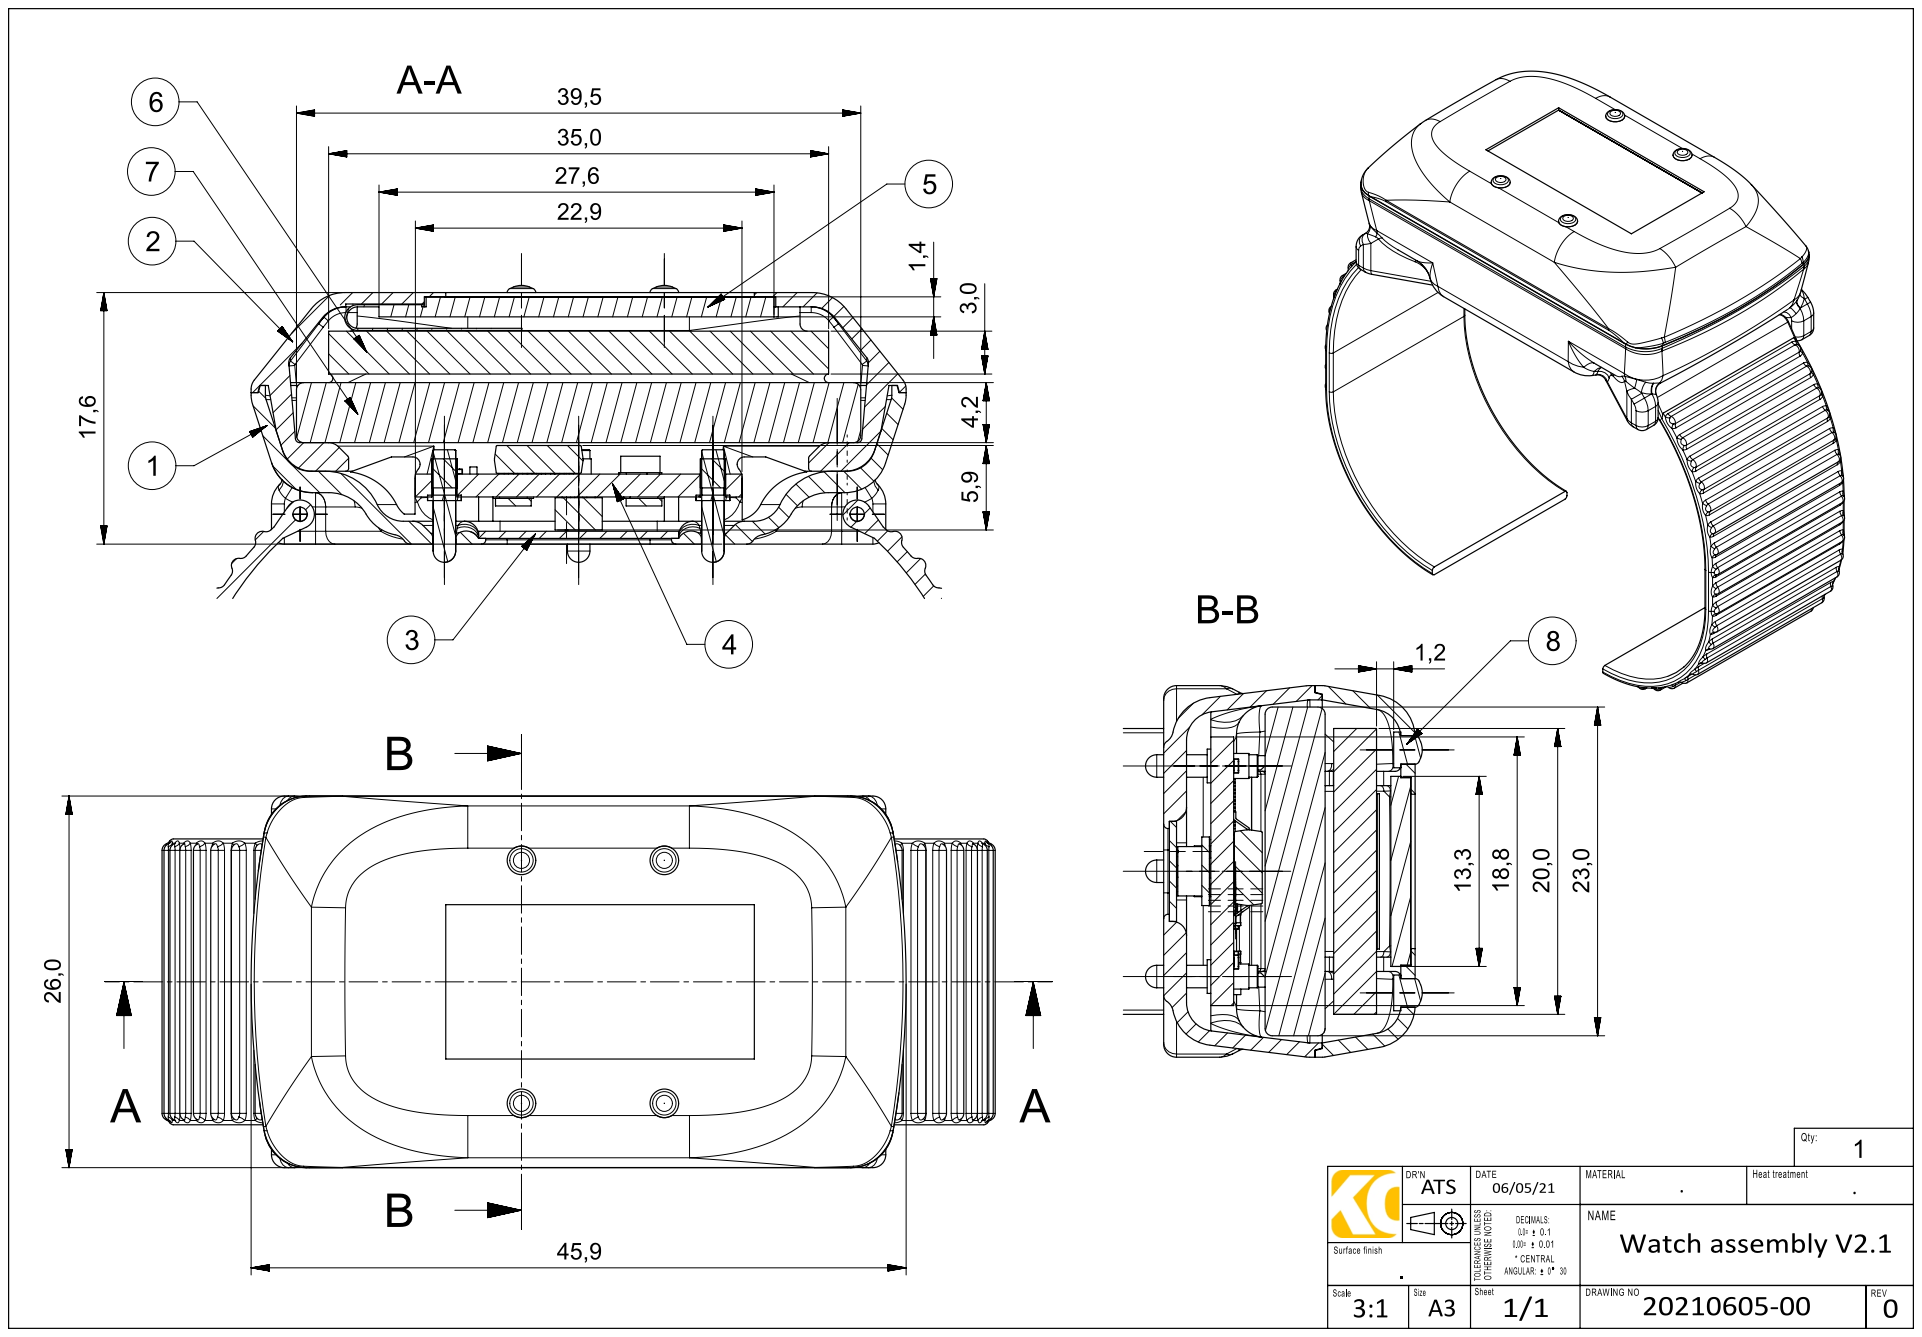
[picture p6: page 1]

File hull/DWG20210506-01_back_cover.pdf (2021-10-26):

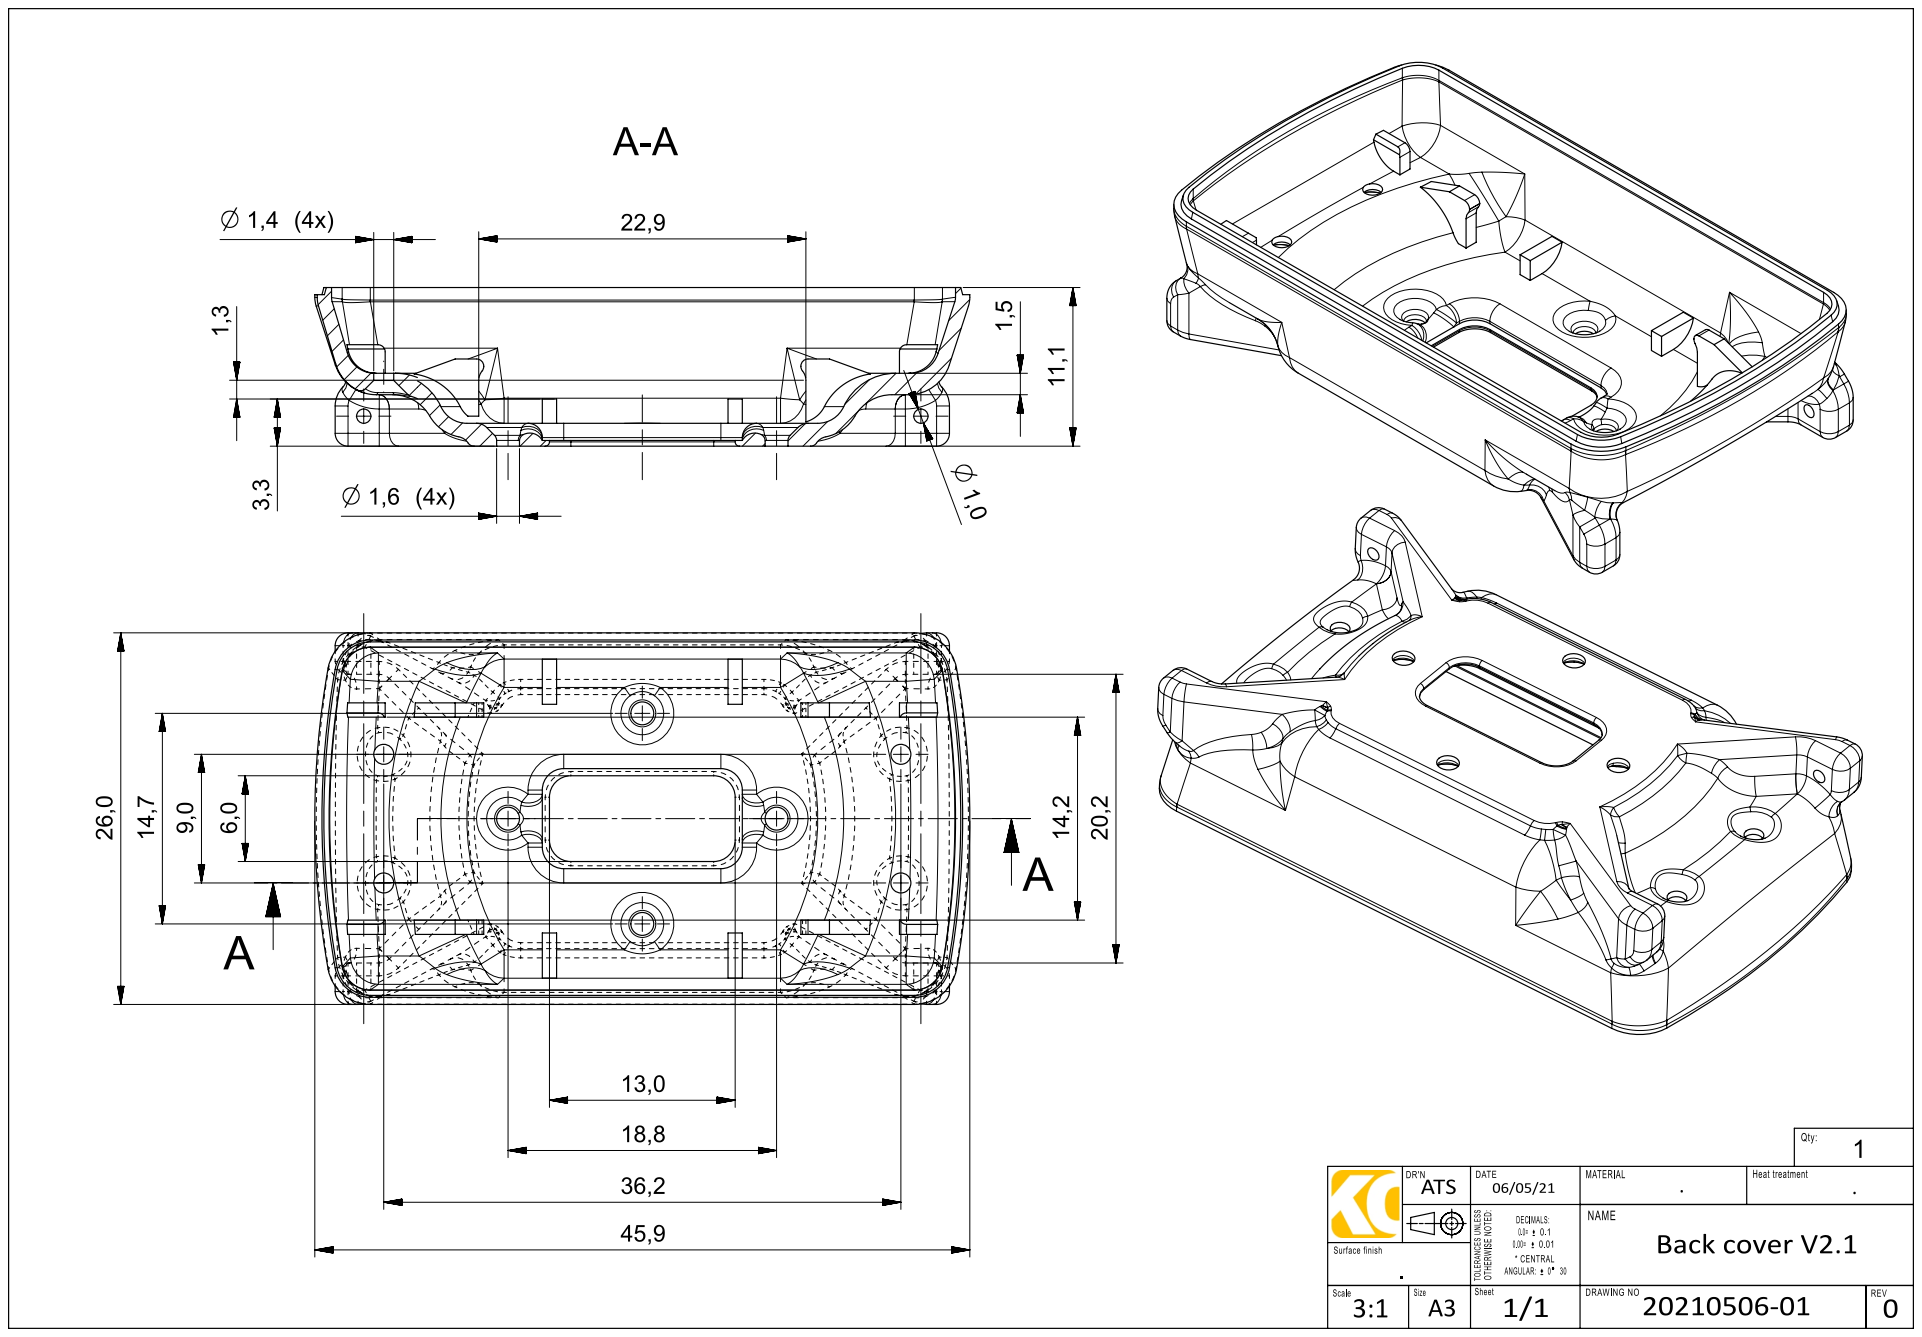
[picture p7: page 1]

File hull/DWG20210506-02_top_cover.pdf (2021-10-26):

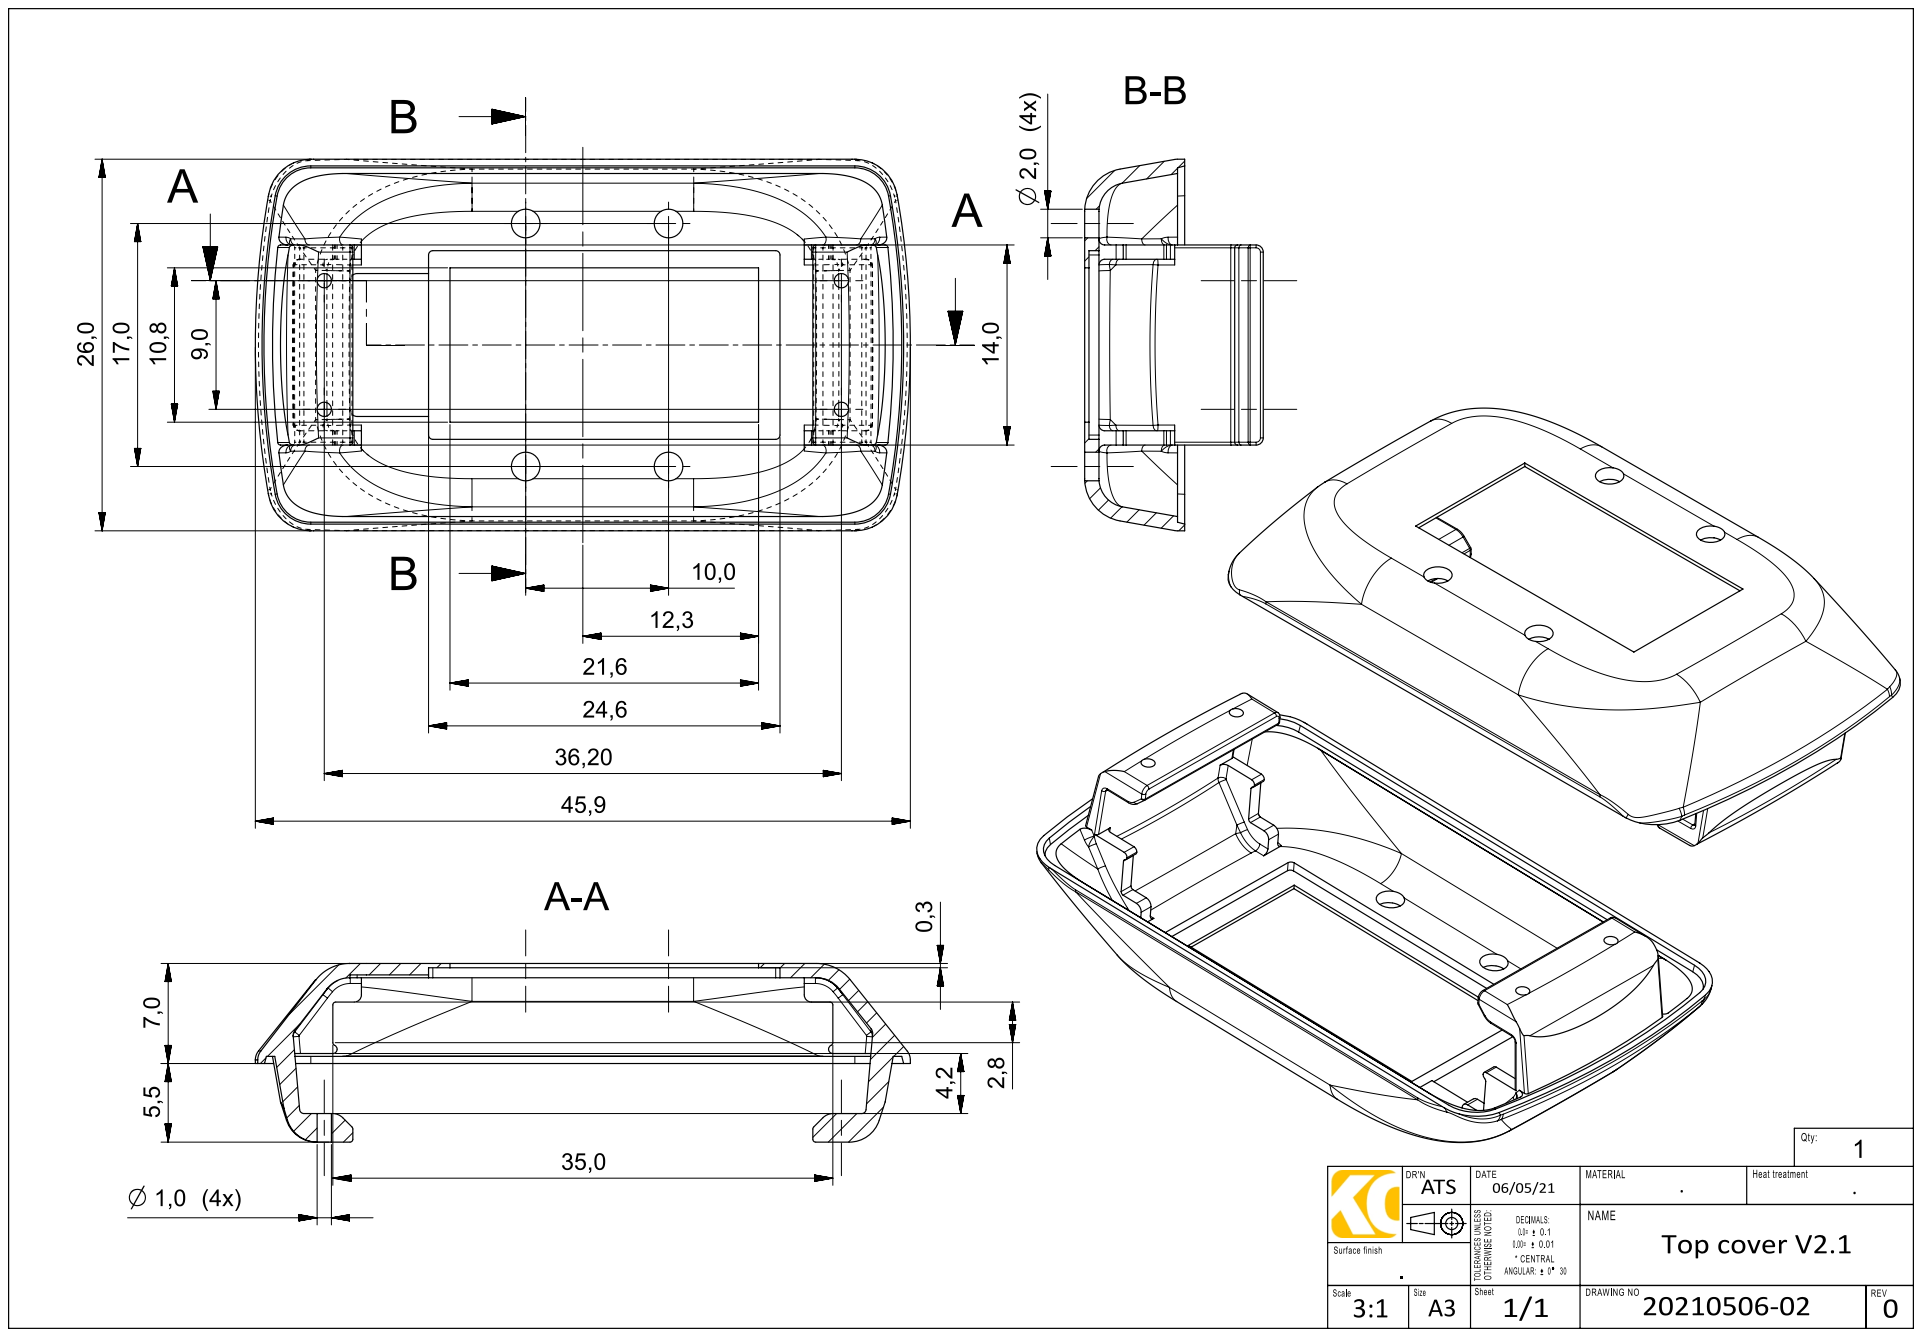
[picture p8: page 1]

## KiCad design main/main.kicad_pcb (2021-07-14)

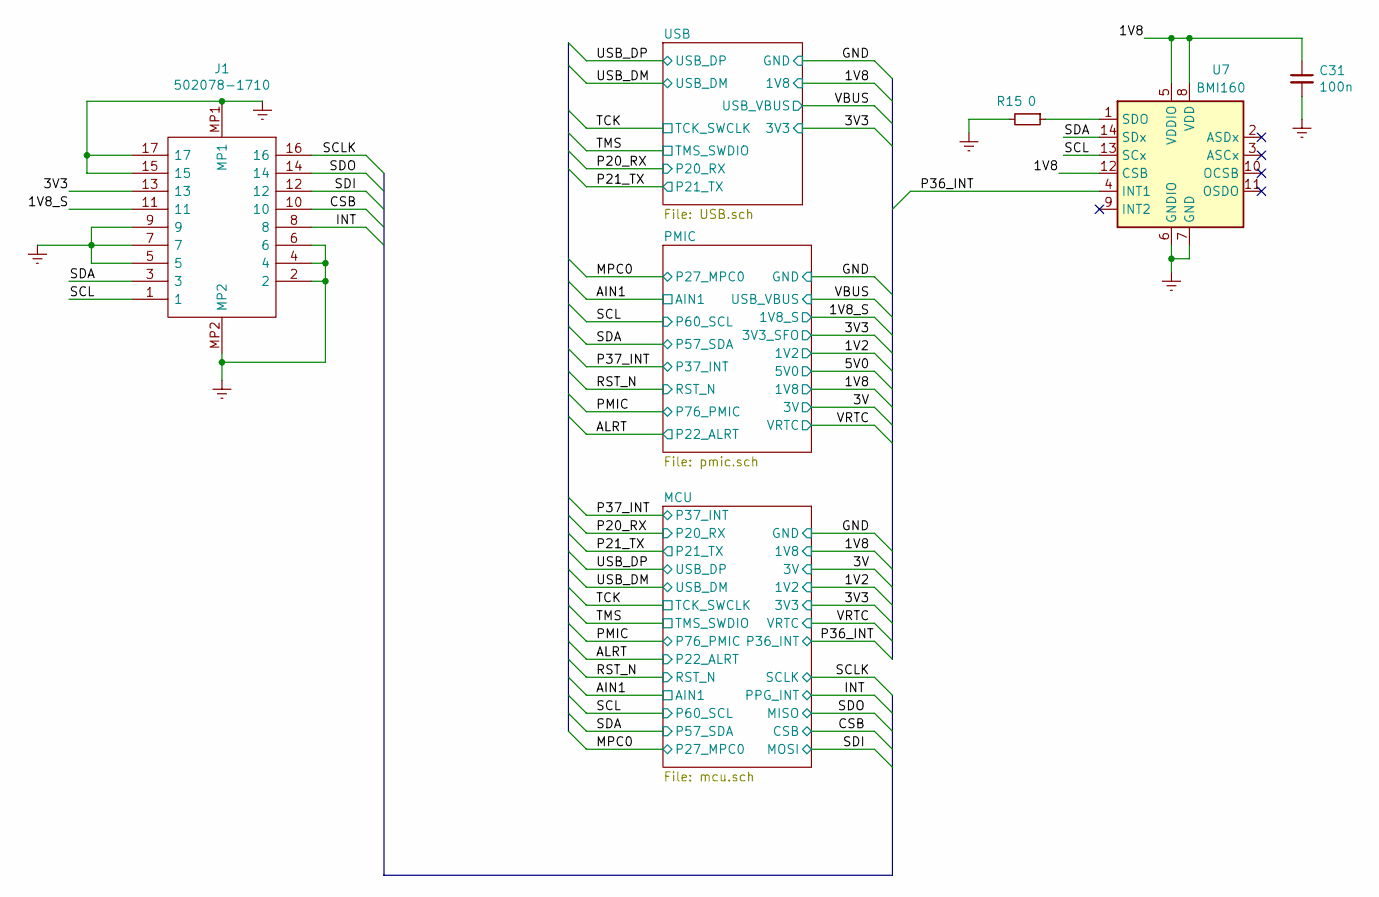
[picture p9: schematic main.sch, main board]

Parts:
C31: 100n; C_0402_1005Metric; Digikey Part Number 311-3340-2-ND
J1: 502078-1710; 5020781710; Mouser Part Number 538-502078-1710
R15: 0; R_0402_1005Metric; Digikey Part Number 541-4062-2-ND
U7: BMI160; Bosch_LGA-14_3x2.5mm_P0.5mm; Digikey Part Number 828-1057-2-ND

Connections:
+1V8: C31.1, U7.5 (VDDIO), U7.8 (VDD), U7.12 (CSB); also elsewhere on the board
+3V3: J1.13; also elsewhere on the board
-BATT: C31.2, J1.2, J1.4, J1.5, J1.6, J1.7, J1.9, J1.15, J1.17, J1.MP1, J1.MP2, R15.2, U7.6 (GNDIO), U7.7 (GND); also elsewhere on the board
/1V8_S: J1.11; also elsewhere on the board
/CSB: J1.10; also elsewhere on the board
/INT: J1.8; also elsewhere on the board
/P36_INT: U7.4 (INT1); also elsewhere on the board
/SCL: J1.1, U7.13 (SCx); also elsewhere on the board
/SCLK: J1.16; also elsewhere on the board
/SDA: J1.3, U7.14 (SDx); also elsewhere on the board
/SDI: J1.12; also elsewhere on the board
/SDO: J1.14; also elsewhere on the board
unnamed: R15.1, U7.1 (SDO)

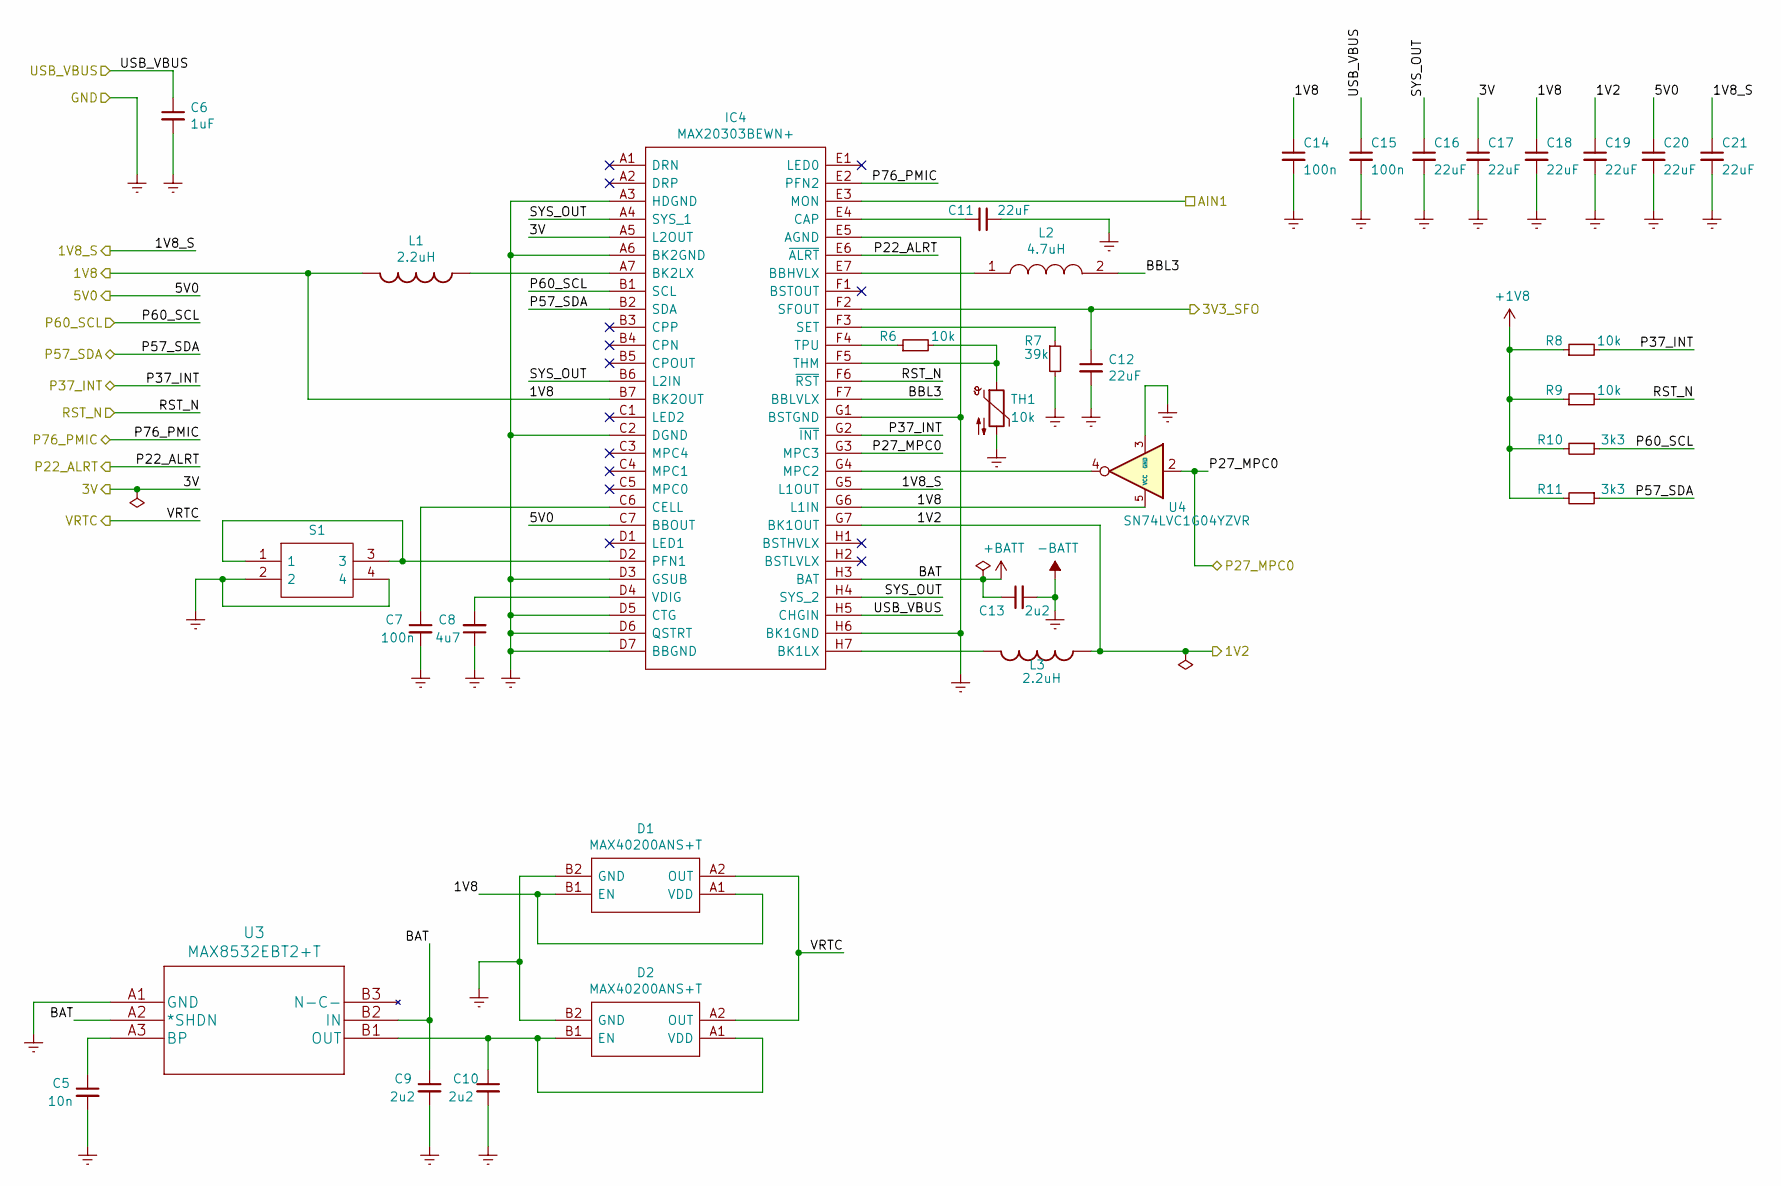
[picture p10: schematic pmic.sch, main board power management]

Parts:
C5: 10n; C_0402_1005Metric; Digikey Part Number 311-3822-2-ND
C6: 1uF; C_0402_1005Metric; Digikey Part Number 311-1438-2-ND
C7, C14, C15: 100n; C_0402_1005Metric; Digikey Part Number 311-3340-2-ND
C8: 4u7; C_0402_1005Metric; Digikey Part Number 311-3476-2-ND
C9, C10, C13: 2u2; C_0402_1005Metric; Digikey Part Number 311-1682-2-ND
C11, C12, C16, C17, C18, C19, C20, C21: 22uF; C_0402_1005Metric
D1, D2: MAX40200ANS+T; BGA4C35P2X2_73X73X50; Manufacturer_Part_Number MAX40200ANS+T; Mouser Part Number 700-MAX40200ANS+T
IC4: MAX20303BEWN+; BGA56C50P7X8_368X418X69; Manufacturer_Part_Number MAX20303BEWN+; Mouser Part Number 700-MAX20303BEWN+
L1, L3: 2.2uH; INDC2016X120N; Digikey Part Number 490-DFE201612E-2R2M=P2TR-ND
L2: 4.7uH; 1285ASH1R0MP2; Manufacturer_Part_Number DFE201610E-4R7M=P2; Mouser Part Number 81-DFE201610E-4R7MP2
R6, R8, R9: 10k; R_0402_1005Metric; Digikey Part Number 541-4276-2-ND
R7: 39k; R_0402_1005Metric; Digikey Part Number 541-4931-2-ND
R10, R11: 3k3; R_0402_1005Metric; Digikey Part Number 541-4080-2-ND
S1: 434153017835; Manufacturer_Part_Number 434153017835; Mouser Part Number 710-434153017835
TH1: 10k; THRMC0603X33N; Digikey Part Number 490-11806-2-ND
U3: MAX8532EBT2+T; MAX8532EBT2&plus_T; Digikey Part Number 2156-MAX8532EBT2+T-ND
U4: SN74LVC1G04YZVR; Digikey Part Number 296-21055-2-ND

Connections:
+1V8: C14.1, C18.1, D1.A1 (VDD), D1.B1 (EN), IC4.B7 (BK2OUT), IC4.G6 (L1IN), L1.1, R8.1, R9.1, R10.2, R11.2, U4.5 (VCC); also elsewhere on the board
+3V3: C12.1, IC4.F2 (SFOUT); also elsewhere on the board
+BATT: C9.1, C13.1, IC4.H3 (BAT), U3.A2 (*SHDN), U3.B2 (IN)
-BATT: C5.2, C6.2, C7.2, C8.1, C9.2, C10.2, C11.1, C12.2, C13.2, C14.2, C15.2, C16.2, C17.2, C18.2, C19.2, C20.2, C21.2, D1.B2 (GND), D2.B2 (GND), IC4.A3 (HDGND), IC4.A6 (BK2GND), IC4.C2 (DGND), IC4.D3 (GSUB), IC4.D5 (CTG), IC4.D6 (QSTRT), IC4.D7 (BBGND), IC4.E5 (AGND), IC4.G1 (BSTGND), IC4.H6 (BK1GND), R7.2, S1.2, S1.4, TH1.2, U3.A1 (GND), U4.3 (GND); also elsewhere on the board
/1V2: C19.1, IC4.G7 (BK1OUT), L3.2; also elsewhere on the board
/1V8_S: C21.1, IC4.G5 (L1OUT); also elsewhere on the board
/3V: C17.1, IC4.A5 (L2OUT); also elsewhere on the board
/5V0: C20.1, IC4.C7 (BBOUT)
/AIN1: IC4.E3 (MON); also elsewhere on the board
/ALRT: IC4.E6 (~ALRT); also elsewhere on the board
/MPC0: IC4.G3 (MPC3), U4.2; also elsewhere on the board
/P37_INT: IC4.G2 (~INT), R8.2; also elsewhere on the board
/PMIC: IC4.E2 (PFN2); also elsewhere on the board
/PMIC/BBL3: IC4.F7 (BBLVLX), L2.2
/PMIC/SYS_OUT: C16.1, IC4.A4 (SYS_1), IC4.B6 (L2IN), IC4.H4 (SYS_2)
/RST_N: IC4.F6 (~RST), R9.2; also elsewhere on the board
/SCL: IC4.B1 (SCL), R10.1; also elsewhere on the board
/SDA: IC4.B2 (SDA), R11.1; also elsewhere on the board
/VRTC: D1.A2 (OUT), D2.A2 (OUT); also elsewhere on the board
unnamed: C5.1, U3.A3 (BP)
unnamed: C7.1, IC4.C6 (CELL)
unnamed: C8.2, IC4.D4 (VDIG)
unnamed: C10.1, D2.A1 (VDD), D2.B1 (EN), U3.B1 (OUT)
unnamed: C11.2, IC4.E4 (CAP)
unnamed: IC4.A7 (BK2LX), L1.2
unnamed: IC4.D2 (PFN1), S1.1, S1.3
unnamed: IC4.E7 (BBHVLX), L2.1
unnamed: IC4.F3 (SET), R7.1
unnamed: IC4.F4 (TPU), R6.1
unnamed: IC4.F5 (THM), R6.2, TH1.1
unnamed: IC4.G4 (MPC2), U4.4
unnamed: IC4.H7 (BK1LX), L3.1
VBUS: C6.1, C15.1, IC4.H5 (CHGIN); also elsewhere on the board

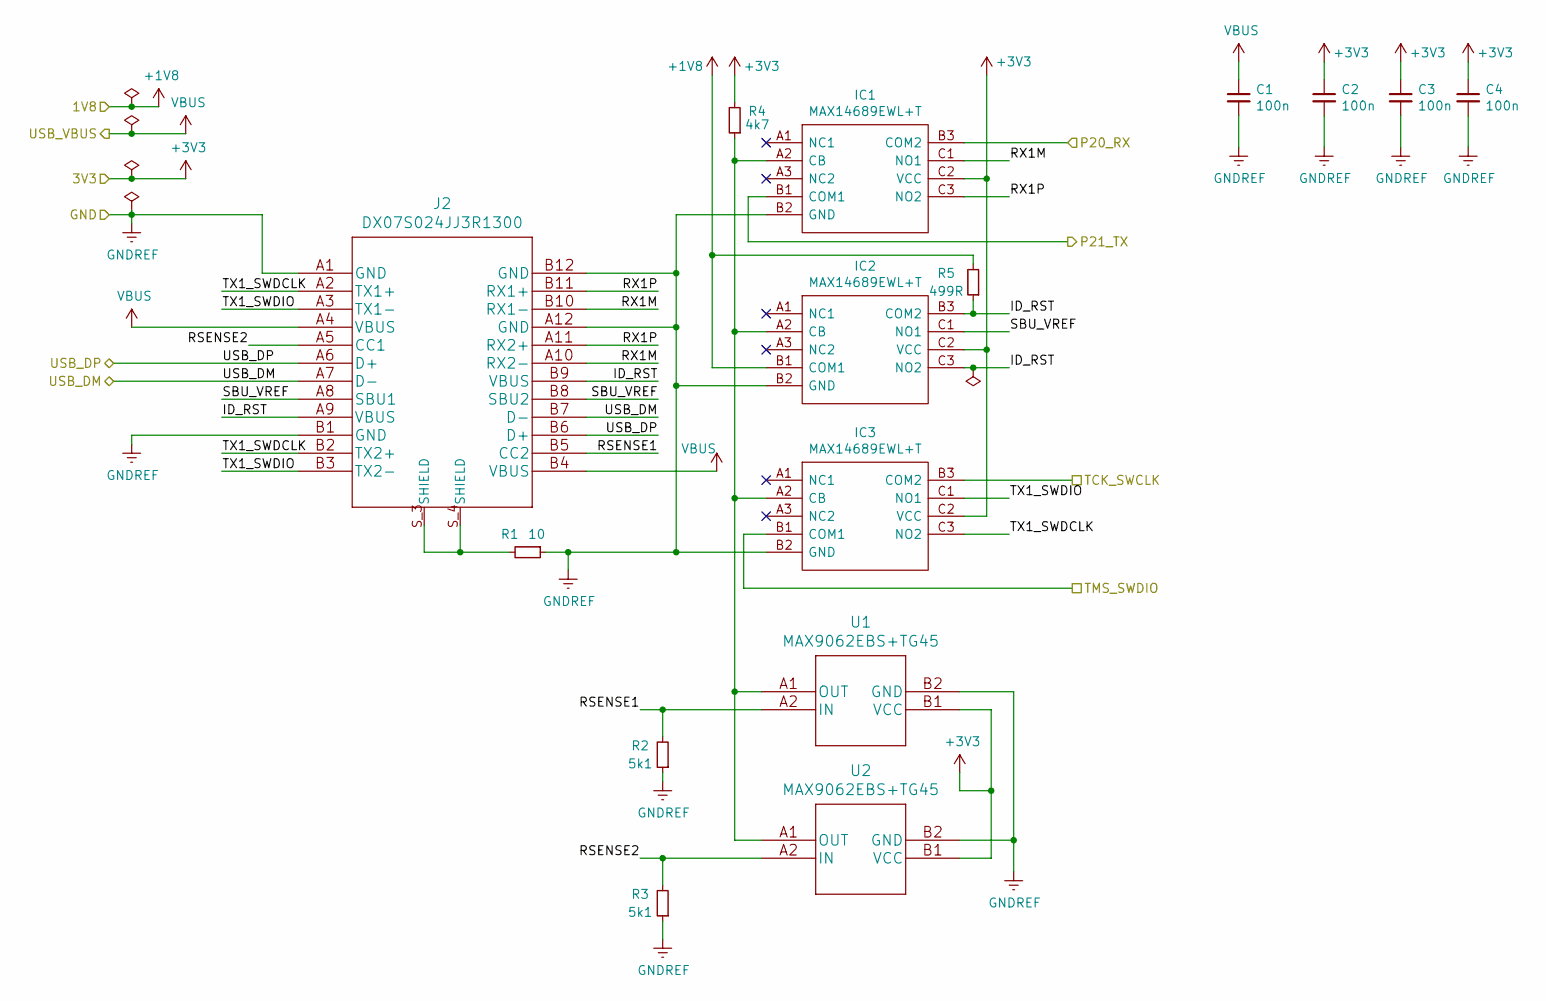
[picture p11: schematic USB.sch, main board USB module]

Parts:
C1, C2, C3, C4: 100n; C_0402_1005Metric; Digikey Part Number 311-3340-2-ND
IC1, IC2, IC3: MAX14689EWL+T; BGA9C40P3X3_124X124X69; Manufacturer_Part_Number MAX14689EWL+T; Mouser Part Number 700-MAX14689EWL+T
J2: DX07S024JJ3R1300; Digikey Part Number 670-2846-2-ND
R1: 10; R_0402_1005Metric; Digikey Part Number 541-3964-2-ND
R2, R3: 5k1; R_0402_1005Metric; Digikey Part Number 541-4069-2-ND
R4: 4k7; R_0402_1005Metric; Digikey Part Number 541-3963-2-ND
R5: 499R; R_0402_1005Metric; Digikey Part Number 541-4007-2-ND
U1, U2: MAX9062EBS+TG45; MAX9062EBS&plus_TG45; Digikey Part Number MAX9062EBS+TG45-ND

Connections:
+1V8: IC2.B1 (COM1), R5.2; also elsewhere on the board
+3V3: C2.1, C3.1, C4.1, IC1.C2 (VCC), IC2.C2 (VCC), IC3.C2 (VCC), R4.2, U1.B1 (VCC), U2.B1 (VCC); also elsewhere on the board
-BATT: C1.2, C2.2, C3.2, C4.2, IC1.B2 (GND), IC2.B2 (GND), IC3.B2 (GND), J2.A1 (GND), J2.A12 (GND), J2.B1 (GND), J2.B12 (GND), R1.1, R2.1, R3.1, U1.B2 (GND), U2.B2 (GND); also elsewhere on the board
/P20_RX: IC1.B3 (COM2); also elsewhere on the board
/P21_TX: IC1.B1 (COM1); also elsewhere on the board
/TCK: IC3.B3 (COM2); also elsewhere on the board
/TMS: IC3.B1 (COM1); also elsewhere on the board
/USB/ID_RST: IC2.B3 (COM2), IC2.C3 (NO2), J2.A9 (VBUS), J2.B9 (VBUS), R5.1
/USB/RSENSE1: J2.B5 (CC2), R2.2, U1.A2 (IN)
/USB/RSENSE2: J2.A5 (CC1), R3.2, U2.A2 (IN)
/USB/RX1M: IC1.C1 (NO1), J2.A10 (RX2-), J2.B10 (RX1-)
/USB/RX1P: IC1.C3 (NO2), J2.A11 (RX2+), J2.B11 (RX1+)
/USB/SBU_VREF: IC2.C1 (NO1), J2.A8 (SBU1), J2.B8 (SBU2)
/USB/TX1_SWDCLK: IC3.C3 (NO2), J2.A2 (TX1+), J2.B2 (TX2+)
/USB/TX1_SWDIO: IC3.C1 (NO1), J2.A3 (TX1-), J2.B3 (TX2-)
/USB_DM: J2.A7 (D-), J2.B7 (D-); also elsewhere on the board
/USB_DP: J2.A6 (D+), J2.B6 (D+); also elsewhere on the board
unnamed: IC1.A2 (CB), IC2.A2 (CB), IC3.A2 (CB), R4.1, U1.A1 (OUT), U2.A1 (OUT)
unnamed: J2.S_3 (SHIELD), J2.S_4 (SHIELD), R1.2
VBUS: C1.1, J2.A4 (VBUS), J2.B4 (VBUS); also elsewhere on the board

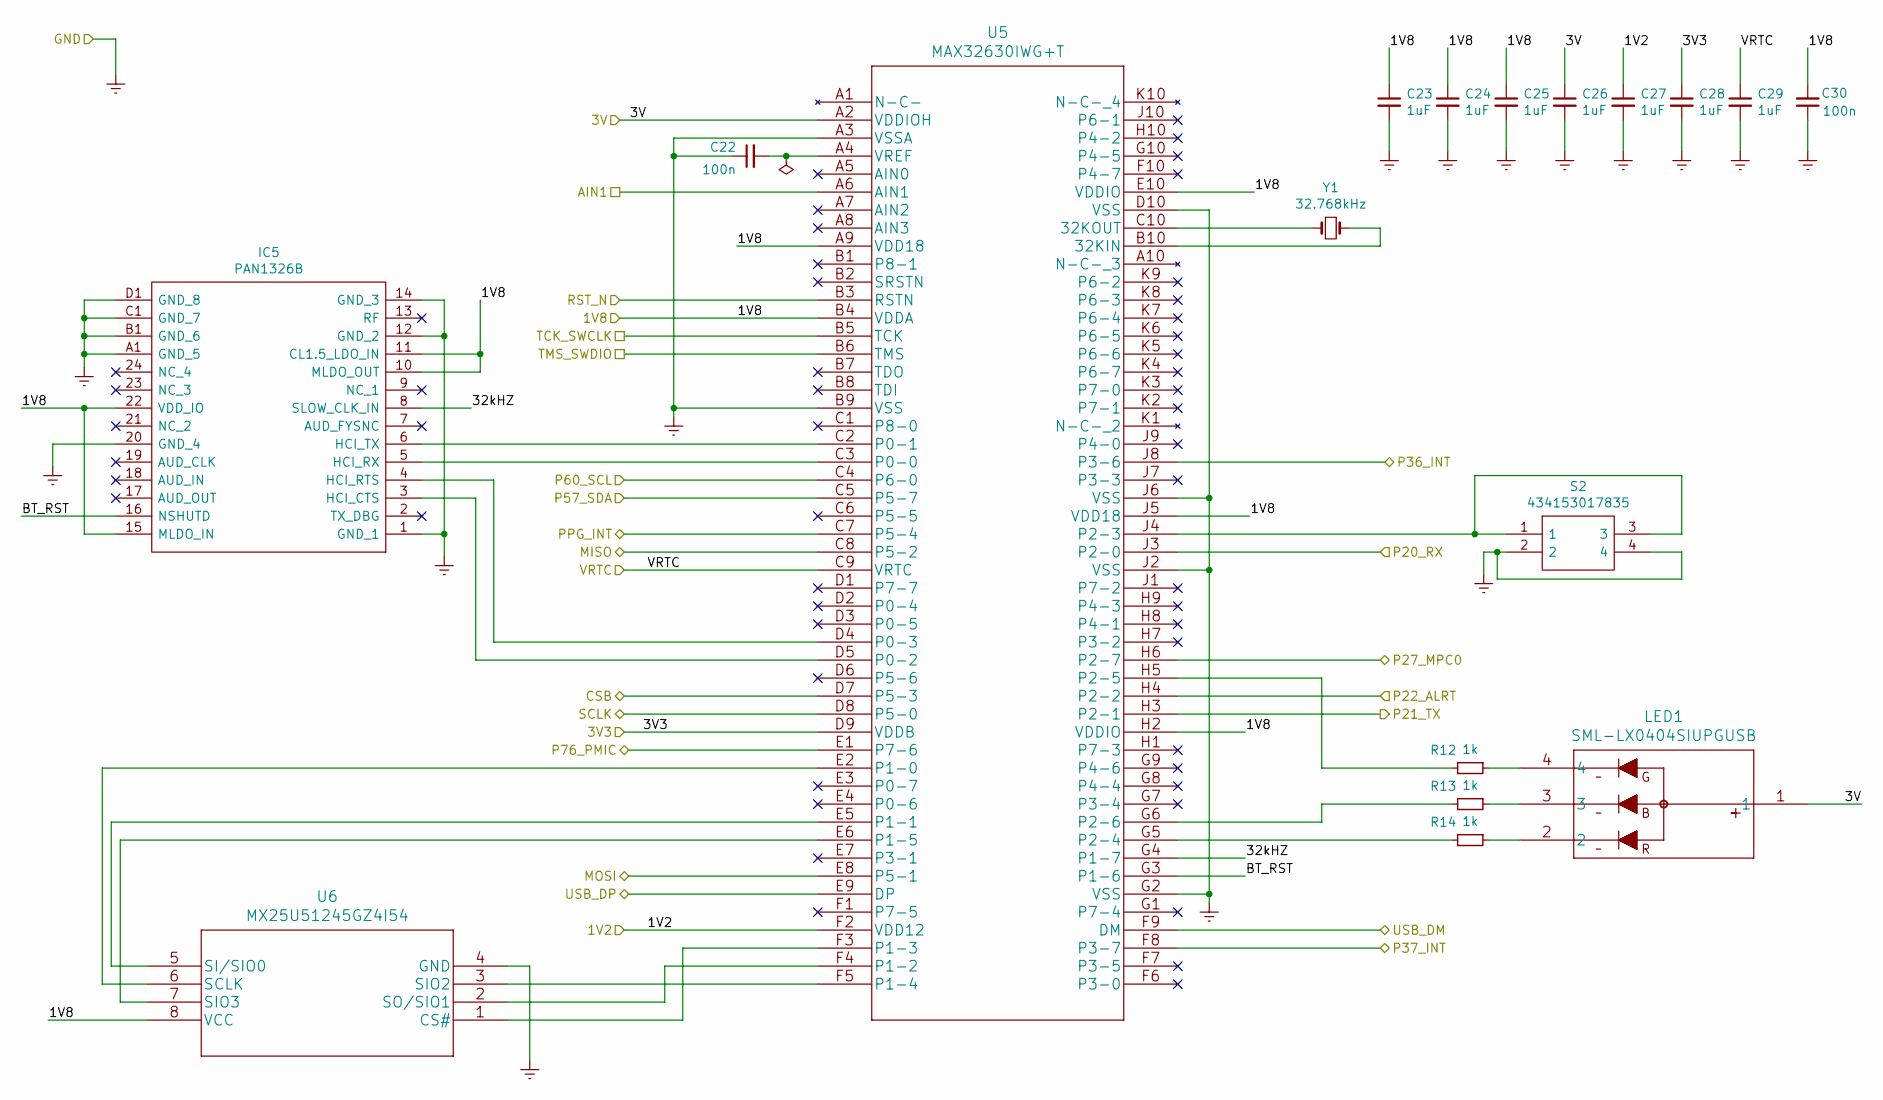
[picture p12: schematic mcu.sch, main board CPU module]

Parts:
C22, C30: 100n; C_0402_1005Metric; Digikey Part Number 311-3340-2-ND
C23, C24, C25, C26, C27, C28, C29: 1uF; C_0402_1005Metric; Digikey Part Number 311-1438-2-ND
IC5: PAN1326B; Manufacturer_Part_Number PAN1326B; Digikey Part Number P16860TR-ND
LED1: SML-LX0404SIUPGUSB; Digikey Part Number 67-2125-1-ND
R12, R13, R14: 1k; R_0402_1005Metric; Digikey Part Number 541-4279-2-ND
S2: 434153017835; Manufacturer_Part_Number 434153017835; Mouser Part Number 710-434153017835
U5: MAX32630IWG+T; MAX32630IWG&plus_T; Digikey Part Number MAX32630IWG+TCT-ND
U6: MX25U51245GZ4I54; Digikey Part Number 1092-1252-ND
Y1: 32.768kHz; XTAL320X150X90; Digikey Part Number 535-11898-1-ND

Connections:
+1V8: C23.1, C24.1, C25.1, C30.2, IC5.10 (MLDO_OUT), IC5.11 (CL1.5_LDO_IN), IC5.15 (MLDO_IN), IC5.22 (VDD_IO), U5.A9 (VDD18), U5.B4 (VDDA), U5.E10 (VDDIO), U5.H2 (VDDIO), U5.J5 (VDD18), U6.8 (VCC); also elsewhere on the board
+3V3: C28.1, U5.D9 (VDDB); also elsewhere on the board
-BATT: C22.1, C23.2, C24.2, C25.2, C26.2, C27.2, C28.2, C29.2, C30.1, IC5.1 (GND_1), IC5.12 (GND_2), IC5.14 (GND_3), IC5.20 (GND_4), IC5.A1 (GND_5), IC5.B1 (GND_6), IC5.C1 (GND_7), IC5.D1 (GND_8), S2.2, S2.4, U5.A3 (VSSA), U5.B9 (VSS), U5.D10 (VSS), U5.G2 (VSS), U5.J2 (VSS), U5.J6 (VSS), U6.4 (GND); also elsewhere on the board
/1V2: C27.1, U5.F2 (VDD12); also elsewhere on the board
/3V: C26.1, LED1.1, U5.A2 (VDDIOH); also elsewhere on the board
/AIN1: U5.A6 (AIN1); also elsewhere on the board
/ALRT: U5.H4 (P2-2); also elsewhere on the board
/CSB: U5.D7 (P5-3); also elsewhere on the board
/INT: U5.C7 (P5-4); also elsewhere on the board
/MCU/32kHZ: IC5.8 (SLOW_CLK_IN), U5.G4 (P1-7)
/MCU/BT_RST: IC5.16 (NSHUTD), U5.G3 (P1-6)
/MPC0: U5.H6 (P2-7); also elsewhere on the board
/P20_RX: U5.J3 (P2-0); also elsewhere on the board
/P21_TX: U5.H3 (P2-1); also elsewhere on the board
/P36_INT: U5.J8 (P3-6); also elsewhere on the board
/P37_INT: U5.F8 (P3-7); also elsewhere on the board
/PMIC: U5.E1 (P7-6); also elsewhere on the board
/RST_N: U5.B3 (RSTN); also elsewhere on the board
/SCL: U5.C4 (P6-0); also elsewhere on the board
/SCLK: U5.D8 (P5-0); also elsewhere on the board
/SDA: U5.C5 (P5-7); also elsewhere on the board
/SDI: U5.E8 (P5-1); also elsewhere on the board
/SDO: U5.C8 (P5-2); also elsewhere on the board
/TCK: U5.B5 (TCK); also elsewhere on the board
/TMS: U5.B6 (TMS); also elsewhere on the board
/USB_DM: U5.F9 (DM); also elsewhere on the board
/USB_DP: U5.E9 (DP); also elsewhere on the board
/VRTC: C29.1, U5.C9 (VRTC); also elsewhere on the board
unnamed: C22.2, U5.A4 (VREF)
unnamed: IC5.3 (HCI_CTS), U5.D5 (P0-2)
unnamed: IC5.4 (HCI_RTS), U5.D4 (P0-3)
unnamed: IC5.5 (HCI_RX), U5.C3 (P0-0)
unnamed: IC5.6 (HCI_TX), U5.C2 (P0-1)
unnamed: LED1.2, R14.1
unnamed: LED1.3, R13.1
unnamed: LED1.4, R12.1
unnamed: R12.2, U5.H5 (P2-5)
unnamed: R13.2, U5.G6 (P2-6)
unnamed: R14.2, U5.G5 (P2-4)
unnamed: S2.1, S2.3, U5.J4 (P2-3)
unnamed: U5.B10 (32KIN), Y1.1
unnamed: U5.C10 (32KOUT), Y1.2
unnamed: U5.E2 (P1-0), U6.6 (SCLK)
unnamed: U5.E5 (P1-1), U6.5 (SI/SIO0)
unnamed: U5.E6 (P1-5), U6.7 (SIO3)
unnamed: U5.F3 (P1-3), U6.1 (CS#)
unnamed: U5.F4 (P1-2), U6.2 (SO/SIO1)
unnamed: U5.F5 (P1-4), U6.3 (SIO2)

Board: 6 copper layers, 70 parts (1 on the bottom side), 77 nets, no tracks yet.

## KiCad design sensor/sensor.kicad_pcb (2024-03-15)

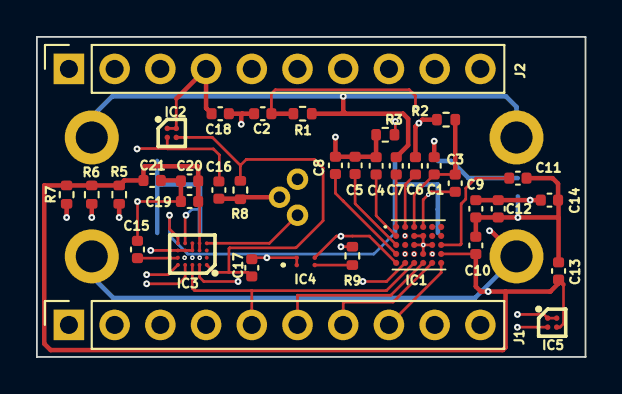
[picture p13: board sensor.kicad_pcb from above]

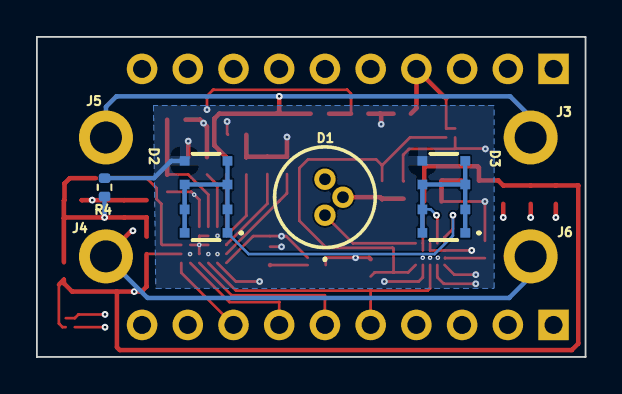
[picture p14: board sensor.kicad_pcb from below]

Board: 4 copper layers, 30.5 x 17.8 mm, 44 parts (8 on the bottom side), 33 nets.

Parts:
C1, C2: 10pF; C_0402_1005Metric
C3: 47pF; C_0402_1005Metric
C4, C14, C15, C17, C18, C21: 1uF; C_0402_1005Metric
C5, C8, C12, C13, C16, C20: 10uF; C_0402_1005Metric
C6, C7: 47nF; C_0402_1005Metric
C9, C10, C19: 0.1uF; C_0402_1005Metric
C11: 1nF; C_0402_1005Metric
D1: RLD65NZX1-00A; RLD85PZJ400A
D2, D3: VEMD8081
IC1: MAX30002CWV+; MAX30002CWV
IC2: LP5900TLX-2.7_NOPB; BGA4C50P2X2_105X108X68
IC3: MAX86141ENP+T; BGA20C40P5X4_205X185X50
IC4: SIT1532AC; SIT1532ACJ5DCC32768D
IC5: LP5900TLX-1.8_NOPB; BGA4C50P2X2_105X108X68
J1, J2: Conn_01x10_Female; PinSocket_1x10_P2.54mm_Vertical
J3, J4, J5, J6: Probe_01_male
R1, R2: 200; R_0402_1005Metric
R3: 324k; R_0402_1005Metric
R4, R8, R9: 0; R_0402_1005Metric
R5, R6, R7: 1k; R_0402_1005Metric

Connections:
+1V8: C10.1, C13.1, C19.1, C20.1, C21.1, IC1.D6 (DVDD), IC1.E1 (AVDD), IC3.C2 (VDD_DIG), IC3.D2 (VDD_ANA), IC4.3 (VDD), IC5.B2 (OUT), R5.2, R6.2, R7.2
+3.3V: C9.1, C12.1, C14.1, C18.1, IC1.D3 (OVDD), IC2.A1 (EN), IC2.A2 (IN), IC5.A1 (EN), IC5.A2 (IN), J2.4
/2V7: C17.1, IC2.B2 (OUT), IC3.A1 (VLED), R8.2
/CSB: IC3.A5 (CSB), J2.5
/CSB2: IC1.E6 (CSB), J1.8
/FCLK: IC1.D5 (FCLK), R9.2
/INT: IC3.B2 (~INT), J2.8, R5.1
/INT2B: IC1.E2 (INT2B), J2.9
/INTB: IC1.D2 (INTB), J2.10
/SCLK: IC1.E5 (SCLK), IC3.A2 (SCLK), J1.7
/SDI: IC1.E4 (SDI), IC3.A4 (SDI), J1.6
/SDO: IC1.E3 (SDO), IC3.A3 (SDO), J1.5
GNDREF: C1.1, C2.1, C4.2, C5.2, C8.2, C9.2, C10.2, C11.2, C12.2, C13.2, C14.2, C15.2, C16.2, C17.2, C18.2, C19.2, C20.2, C21.2, IC1.B3 (AGND_1), IC1.B4 (AGND_2), IC1.C3 (AGND_3), IC1.C4 (AGND_4), IC1.C5 (DGND), IC1.D4 (AGND_5), IC2.B1 (GND), IC4.1 (GND_1), IC4.4 (GND_2), IC5.B1 (GND), J1.10, J2.2, R3.2, R4.2
GNDS: D2.5 (PD_PIN_5_ANODE), D3.5 (PD_PIN_5_ANODE), IC3.C3 (GND_DIG), IC3.C4 (GND_ANA), IC3.C5 (PD_GND), IC3.D3 (PGND), R4.1
unnamed: C16.1, D1.3 (COMMON), R8.1
unnamed: D1.1 (K_LD), IC3.D1 (LED1_DRV)
unnamed: D2.1 (PD_PIN_1_CATHODE), D2.2 (PD_PIN_2_CATHODE), D2.3 (PD_PIN_3_CATHODE), D2.4 (PD_PIN_4_CATHODE), D2.6 (PD_PIN_6_CATHODE), D2.7 (PD_PIN_7_CATHODE), D2.8 (PD_PIN_8_CATHODE), IC3.D5 (PD1_IN)
unnamed: D3.1 (PD_PIN_1_CATHODE), D3.2 (PD_PIN_2_CATHODE), D3.3 (PD_PIN_3_CATHODE), D3.4 (PD_PIN_4_CATHODE), D3.6 (PD_PIN_6_CATHODE), D3.7 (PD_PIN_7_CATHODE), D3.8 (PD_PIN_8_CATHODE), IC3.D4 (PD2_IN)
unnamed: C1.2, C3.2, IC1.A3 (BIN), R2.2
unnamed: C2.2, C3.1, IC1.A4 (BIP), R1.2
unnamed: C11.1, IC1.C6 (CPLL)
unnamed: C6.1, IC1.A2 (DRVN)
unnamed: C7.1, IC1.A1 (DRVP)
unnamed: IC1.B2 (RBIAS), R3.1
unnamed: C4.1, IC1.B1 (VBG)
unnamed: C5.1, IC1.C1 (VCM)
unnamed: C8.1, IC1.D1 (VREF)
unnamed: IC3.B3 (GPIO1), R6.1
unnamed: IC3.B4 (GPIO2), R7.1
unnamed: C15.1, IC3.B5 (VREF)
unnamed: IC4.2 (CLK_OUT), R9.1
unnamed: C7.2, J3.1, J5.1, R1.1
unnamed: C6.2, J4.1, J6.1, R2.1

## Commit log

2021-02-27 added crystal and motion sensor
    [main board.sch, mcu.sch, pmic.sch]
2021-02-27 added VRTC power input
    [main board.sch, mcu.sch, pmic.sch]
2021-02-27 added flash and LED
    [main board.sch, mcu.sch, pmic.sch]
2021-02-27 sensor board part numbers review
    [sensor board.sch]
2021-02-27 update sensor board BOM
    [sensor board.csv]
2021-02-27 add some part numbers to main board
    [main board.sch]
2021-02-27 added 100n capacitor
    [USB.sch, main board.sch, mcu.sch, pmic.sch]
2021-02-28 USB PNs
    [USB.sch]
2021-02-28 pmic components
    [pmic.sch]
2021-02-28 mcu parts
    [main board.sch, mcu.sch, pmic.sch]
2021-03-01 main board BOM
    [main board.csv]
2021-03-02 add adapter for sensor board
    [adapter.kicad_pcb, adapter.sch]
2021-03-03 updated sensor board size created netlist for main board
    [sensor board.kicad_pcb]
2021-03-07 - add components to main board - put sensor contacts in the middle of the side edges
    [main board.kicad_pcb, sensor board.kicad_pcb]
2021-03-14 added impedance probe pins
    [sensor board.kicad_pcb, sensor board.sch]
2021-03-21 via/nets definition
    [sensor board.kicad_pcb]
2021-03-22 added buried vias
    [sensor board.kicad_pcb, sensor board.sch]
2021-03-22 finished sensor PCB
    [sensor board.kicad_pcb, sensor board.sch]
2021-03-22 removed unnecessary vias
    [sensor board.kicad_pcb]
2021-03-22 replaced probe wire with zone
    [sensor board.kicad_pcb]
2021-03-31 replace LED, changed board layout and created files for production
    [adapter-B_Cu.gbl, adapter-B_Mask.gbs, adapter-Edge_Cuts.gm1, adapter-F_Cu.gtl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]
2021-04-03 fixed silk labels locations
    [sensor board.kicad_pcb, sensor board.sch]
2021-04-03 renamed project from sensor board -> sensor. This should fix BOM generation error in Windows
    [bom.csv, sensor board-F_SilkS.gto, sensor-B_Cu.gbl, sensor-B_Mask.gbs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]
2021-04-04 renamed main. created board cuts
    [USB.sch, main board.csv, main.kicad_pcb, main.sch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]
2021-04-25 update main board
    [main.kicad_pcb]
2021-04-26 fix resistor type at BOM changed from 0402 to 1005 metric size
    [sensor.csv, sensor.sch]
2021-05-06 Change long SilkB LED caption
    [sensor.kicad_pcb]
2021-07-14 added template data for printing
    [USB.sch, adapter.sch, main.kicad_pcb, main.sch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]
2021-10-26 added hull
    [back_cover_v2_1.stl, back_cover_v2_1.stp, top_cover_v2_1.stl, top_cover_v2_1.stp]
2022-08-31 Added laser and LDO 2.5V
    [adapter.kicad_sch, sensor.kicad_sch]
2022-09-03 Schematic v 2.0 is ready. Can go with PCB design
    [sensor.kicad_pcb, sensor.kicad_sch]
2022-11-10 SIT1532AC-J5-DCC-32.768D.stp oscillator and pins re-number. Fixed board size
    [sensor.kicad_pcb, sensor.kicad_sch]
2022-11-10 Change power for oscillator. Generated annotations and updated board from schematic
    [sensor.kicad_pcb, sensor.kicad_sch]
2022-11-14 BOM check complete
    [sensor.kicad_sch]
2022-11-14 Bottom and signal layers first joints
    [sensor.kicad_pcb]
2022-11-20 new parts alignment based on SPI bus connections
    [sensor.kicad_pcb, sensor.kicad_sch]
2022-11-20 all elements are placed on the board
    [sensor.kicad_pcb, sensor.kicad_sch]
2022-11-20 more wires, only one left
    [sensor.kicad_pcb, sensor.kicad_sch]
2022-11-21 board is finished
    [sensor.kicad_pcb]
2022-11-22 mfg files. 1st run
    [sensor-B_Cu.gbl, sensor-B_Mask.gbs, sensor-B_Paste.gbp, sensor-B_SilkS.gbo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]
2022-11-24 production update 2. added J1,J2 PN and changed via diameters
    [sensor-B_Cu.gbl, sensor-B_Mask.gbs, sensor-B_Paste.gbp, sensor-B_Silkscreen.gbo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]
2022-11-27 3D model updated
    [sensor.step]
2024-03-13 Remove adapter from components
    [adapter-B_Cu.gbl, adapter-B_Mask.gbs, adapter-Edge_Cuts.gm1, adapter-F_Cu.gtl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]
2024-03-14 Clean up for old files. Reposition schematic components to 50mil grid. No errors and warnings for SCH. PCB is next.
    [sensor.kicad_sch, sensor.sch]
2024-03-15 Updated PCB from SCH. Version 2.1 is ready. No functional changes, just cosmetics and conversion to KiCad 8.0
    [sensor.kicad_pcb]
2024-03-22 label external clock
    [sensor.kicad_sch]
2025-04-30 Update README.md
    more details on sensor repository

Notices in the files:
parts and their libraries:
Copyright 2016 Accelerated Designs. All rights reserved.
